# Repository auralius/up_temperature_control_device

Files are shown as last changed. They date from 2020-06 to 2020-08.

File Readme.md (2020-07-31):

This is a repository for the Universitas Pertamina's temperature control device.

The device:

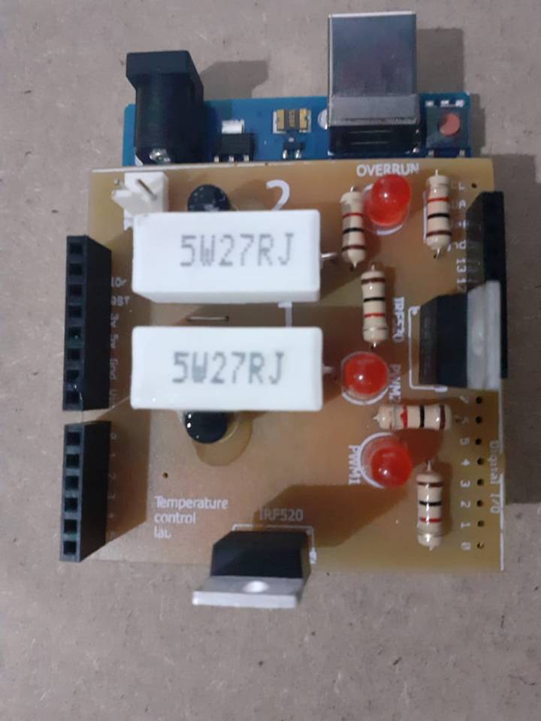
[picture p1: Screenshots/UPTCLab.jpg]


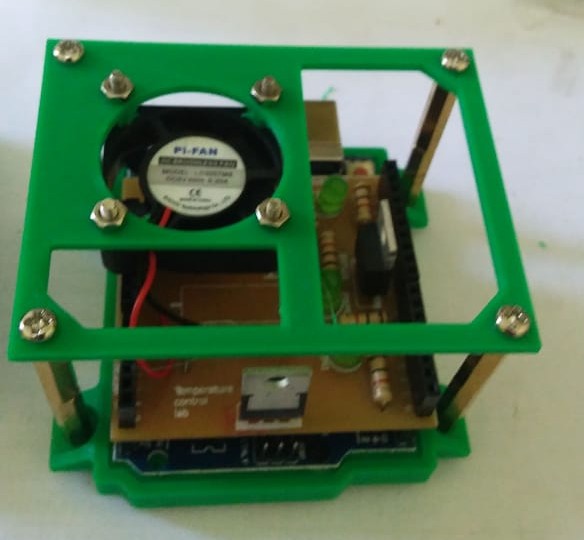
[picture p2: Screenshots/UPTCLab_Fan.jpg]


Features:
- Low cost.
- Open hardware and software, you can make your own.
- Excellent linearity at steady state condition when the temperature is below 120 degress of Celcius.
- Two heaters with two temperature sensors.
- Each heater can be heated to about 140 degrees of Celcius.
- The device is designed such that only the power resistors that become hot. The driving transistors barely get any hot.
- One of te heater can be replaced with a fan.

What you can learn with this device?
- Perform mathematical modeling, starting with the basic Time-Delay-Time-Constant (TDTC) model.
- Analyze the effect of a time delay to a system.
- Linearize the time delay model.
- Understand how a constrained input-output signal contributes to the guarantedness of system stability (a bounded-input and bounded-ouput (BIBO) system).
- Develop and tune a constant gain feedback control.
- Develop and tune a PID control.
- Develop an on-off control with hysteresis.
- Develop a Smith Predictor control.
- Develop more advance model based controls such as the Model Reference Adaptive Control (MRAC).
- Develop multiple-input and multiple-output (MIMO) models and controls.
- Perform system parameter optimizations.
- Develop an energy balance model.
- Calculate convetion rate of the fan as a function of its speed.

The software that is used is MATLAB Simulink with the Arduino support package. It is also possible to use LabVIEW with Linx libraries for the Arduino.

Here some examples:

Pade approximation of a time delay model:

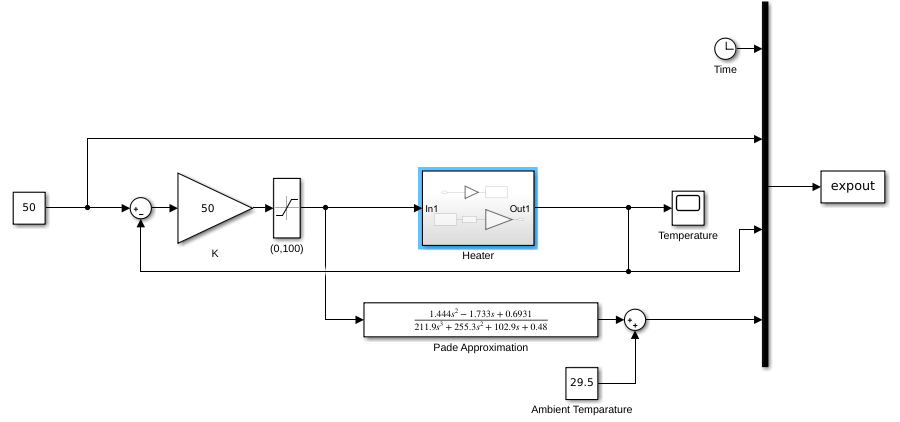
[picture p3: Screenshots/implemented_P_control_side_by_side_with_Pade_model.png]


The TDTC model:

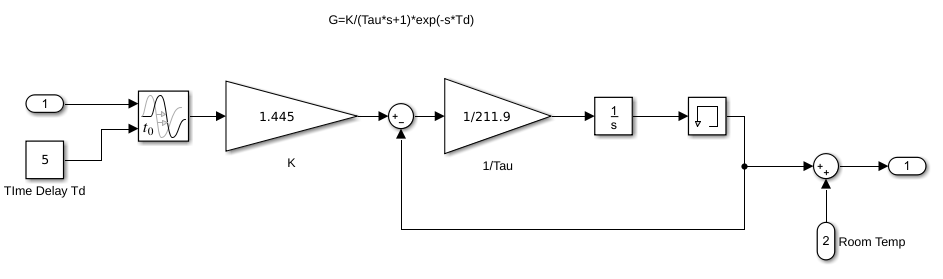
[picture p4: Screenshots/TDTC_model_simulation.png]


The on-off control with hysteresis:

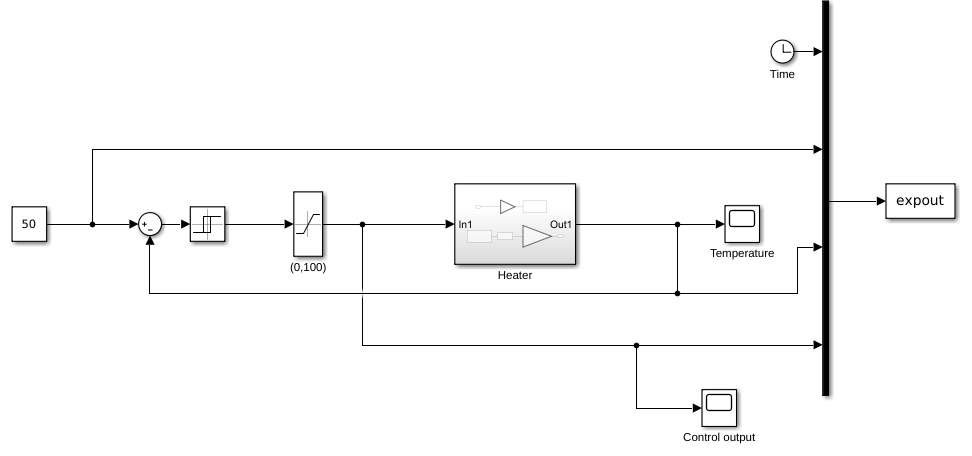
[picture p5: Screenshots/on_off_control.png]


The MRAC with the MIT rule:

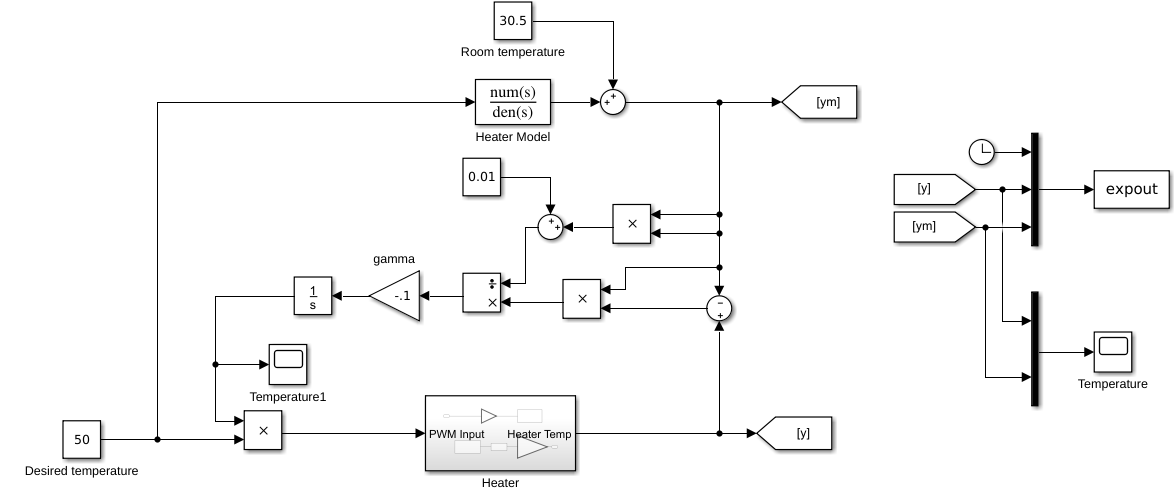
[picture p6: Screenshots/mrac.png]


You might also want to look into the Arduino TCLab from Birgham Young University, where we mainly get our inspiration from: http://apmonitor.com/pdc/index.php/Main/ArduinoTemperatureControl

There is also one from RMIT, Australia: https://journals.sagepub.com/doi/10.1177/0020720919852784

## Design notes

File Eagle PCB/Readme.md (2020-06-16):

Eagle version: 9.5.2 Education

There is a ZIP file containing the GERBER files which have been successfully sent for productions.

The schematic:

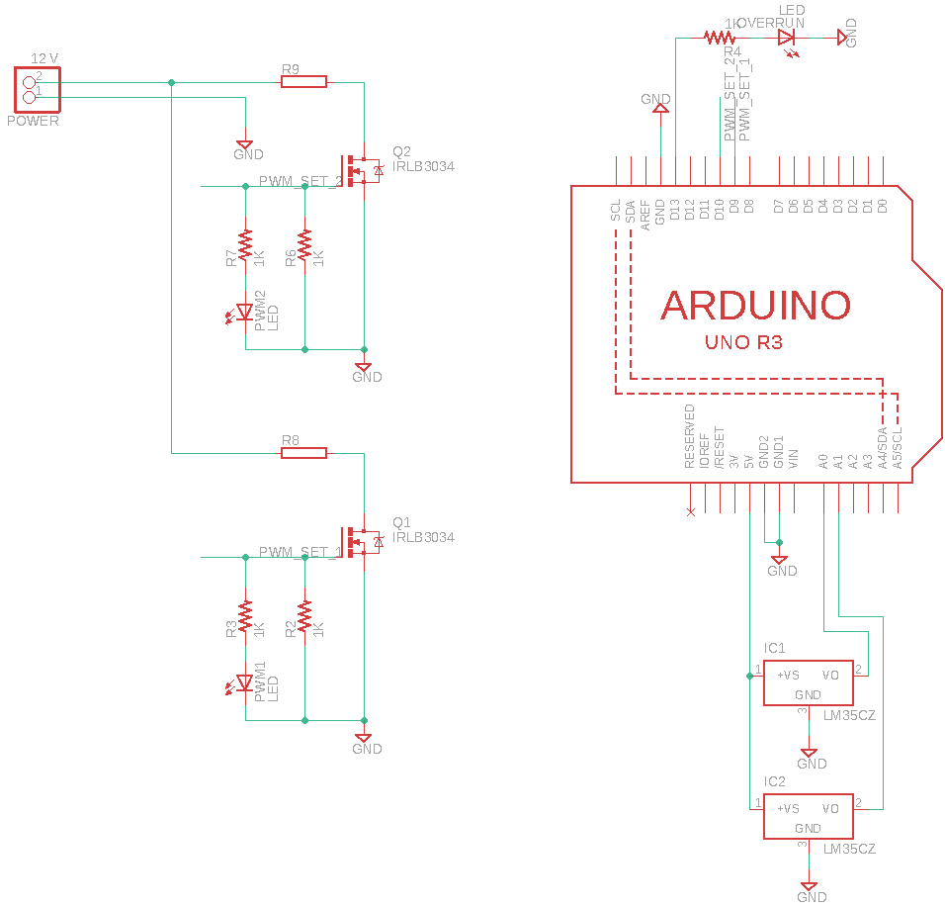
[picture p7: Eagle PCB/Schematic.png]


The PCB:

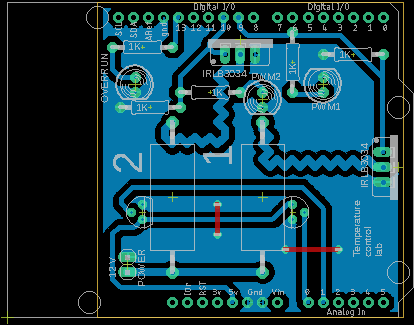
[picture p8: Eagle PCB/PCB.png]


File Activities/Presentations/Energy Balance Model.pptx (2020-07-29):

## Energy Balance Model for the Universitas Pertamina Temperature Control Device

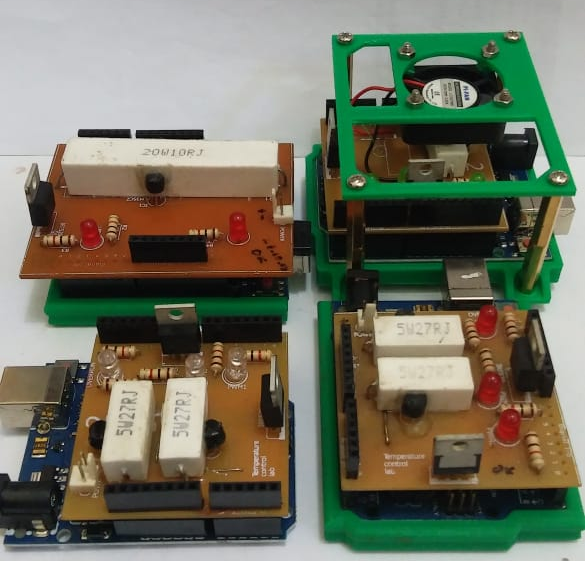
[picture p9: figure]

## Heat Dissipated by a Resistor

P=(V^2)/R
V is the voltage across the resistor
R is the resistance of the resistor
V=α V_(max)
α is the applied PWM percentage (from 0 to 1)
V_(max) is the maximum voltage ( 12 Volts)

## Heat Dissipated by a Resistor

Thus:
P=(αV_(max) ^2)/R
However, since we can not guarantee the correctness of the PWM , V_(max) and R , we then introduce a correcting factor β:
P=β(αV_(max) ^2)/R
We will use an optimization method to find β .

## Energy Balance Model

Heat in = Heat Out + Heat Stored
β(αV_(max) ^2)/R=hA(T_r −T_a )+eσA(T_r^4 −T_a^4 )+mc_r (dT_r)/(dt)

## Energy Balance Model

h is the heat transfer coefficient - W/(m^2 K)
e is the emissivity (from 0 to 1)
σ is the Stefan-Boltzman constant , the value is 5.6703×10^(−8) W/(m^2 K^4 )
c_r is the heat capacity - J/(kg K)
T_r is the temperature of the resistor - K
T_a is the ambient temperature - K

## Finding the Unknown Parameters

Rewrite the energy balance equation in the following form:
mc_r (dT_r)/(dt)=β((αV_(max) )^2)/R+hA(T_a −T_r )+eσA(T_a^4 −T_r^4 )

## Finding the Unknown Parameters

- Known values so far:
  - α is the given PWM command
  - V_(max) =12 Volts
  - R=27 Ohms
  - T_a and T_r are from measurement
  - σ=5.6703×10^(−8)
  - A=0.0008 m^2
  - m=0.005 kg
- Parameters to find:
  - C_r
  - h
  - e , from 0 to 1
  - β , probably from 0 to 1

More or less, measured with a ruler and a scale.

## Results

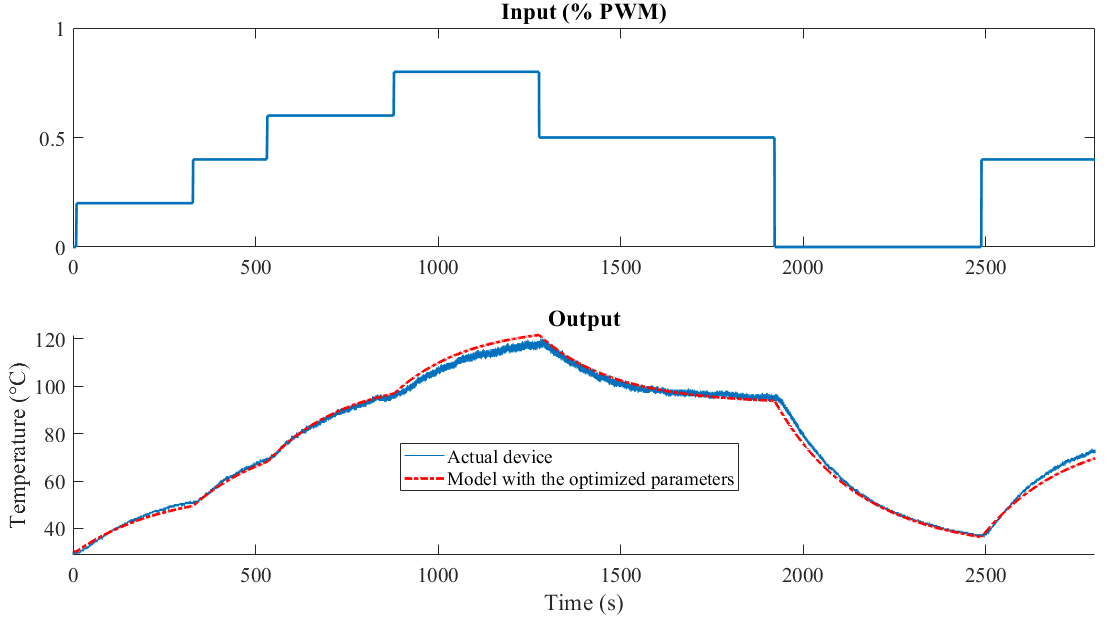
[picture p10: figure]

## Results

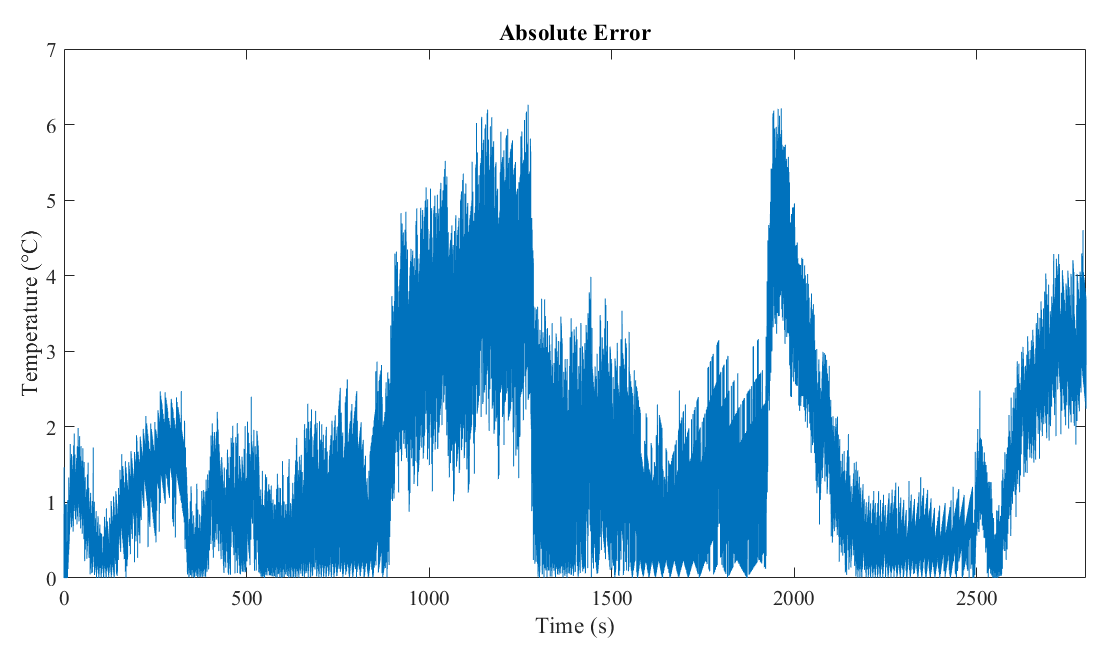
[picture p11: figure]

## Results

By using the fminsearch command (fmincon gives worse estimates)
  - C_r =1015.1584 J/(kg K)
  - h=19.7300 W/(m^2 K)
  - e=0.9047
  - β=0.5131
And the maximum value of the absolute error is less than 7℃ .

## Results

Seriously, no time delay?
Why?

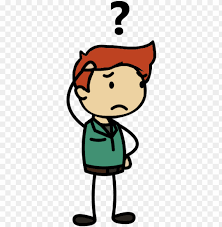
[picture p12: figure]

## Modeling Heat Transfer Coefficient by the Fan

Small fan on top the heater. The speed of the fan can be adjusted,
from 0 (no speed) to 1 (full speed).


## Energy Balance Model

The model becomes:
mc_r (dT_r)/(dt)=β((αV_(max) )^2)/R+(h_1 +γh_2 )A(T_a −T_r )+eσA(T_a^4 −T_r^4 )
h_1 is the heat transfer rate for normal convection while h_2 is by the fan.
γ is the speed of the fan (from 0 to 1).

## Results

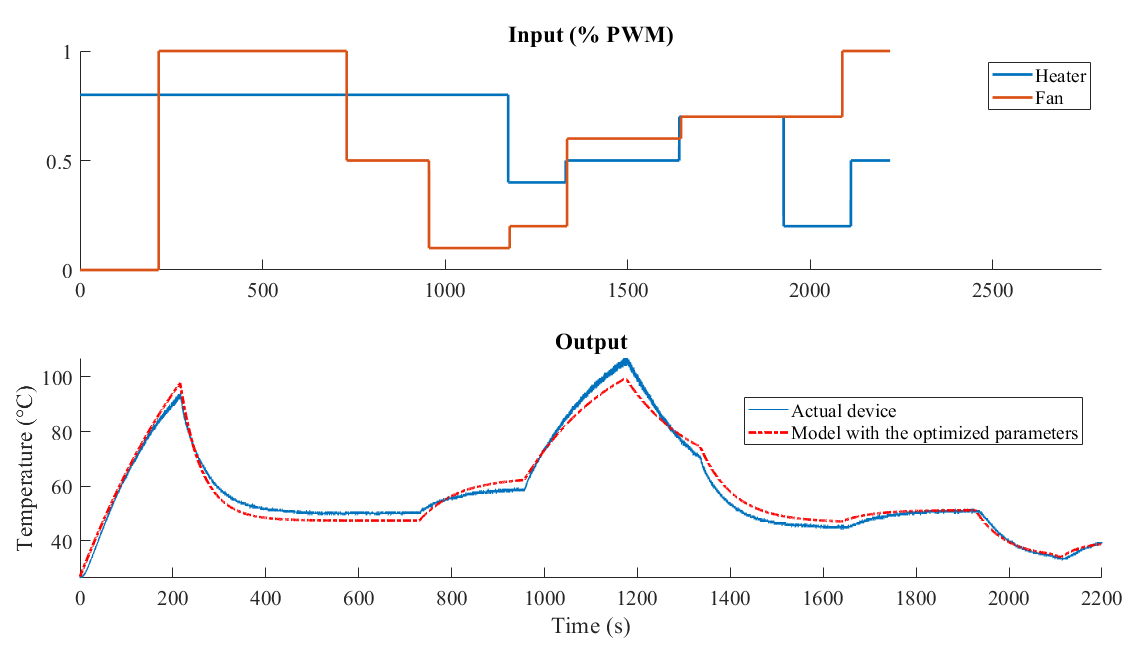
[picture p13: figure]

## Results

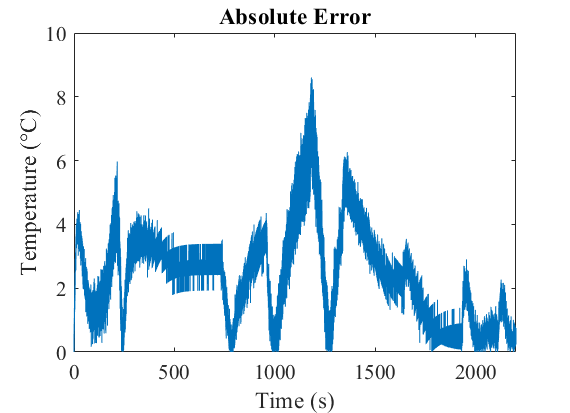
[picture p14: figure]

## Results

By using the fminsearch command:
  - C_r =1014.0626J/(kg K)
  - h_1 =9.7554W/(m^2 K)
  - h_2 =117.8434W/(m^2 K)
  - e=0.9222
  - β=0.5153
And the maximum value of the absolute error is less than 9℃ .
The other parameters get slightly readjusted. Compare them with the previous experiment.
We have some uncertainties here, every time we do the experiment, we might end up with slightly different values.

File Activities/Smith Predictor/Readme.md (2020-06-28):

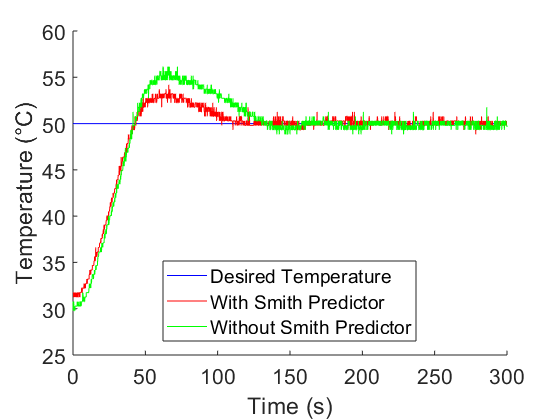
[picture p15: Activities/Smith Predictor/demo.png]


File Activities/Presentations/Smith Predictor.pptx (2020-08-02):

## Smith Predictor

ME
Universitas Pertamina
2020

## Intended Learning Outcomes

- Students learn how a mathematical model can benefit control performance of a system.
- Students can explain how time delay affects a control system performance.

## Tasks

- Implement a constant gain feedback controller and a constant gain feedback controller with Smith Predictor.
- Compare the performance of both controllers.
- Set the gain of both controller to be larger then the jω -crossing gain from the root-locus method.

## The Classical Smith Predictor [1]

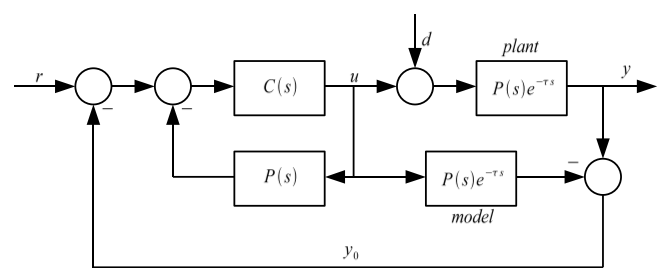
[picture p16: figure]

TC Model

TDTC Model

## Some results

Less overshoot

Less oscillations

## References

[1] O. J. M. Smith, “Closed Control of Loop with Dead Time,” Chemical Engineering Progress 53(5), pp 217-219, 1957

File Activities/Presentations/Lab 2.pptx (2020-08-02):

## First Order Plus Time Delay (FOPTD) Model or Time Delay Time Constant (TDTC) model

ME
Universitas Pertamina
2020

## Step response Experiment

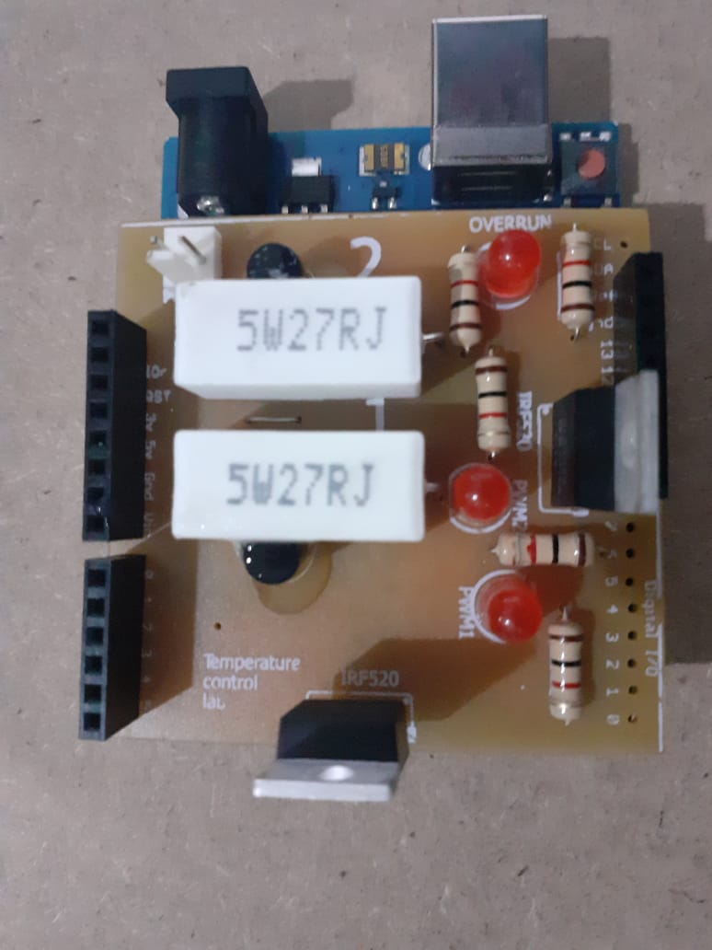
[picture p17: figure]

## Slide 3

- Apply an input of 50%.
- Run the Simulink, record the time, the input and the output.
- Run for at least for 1500 seconds.

## 50% of Input PWM

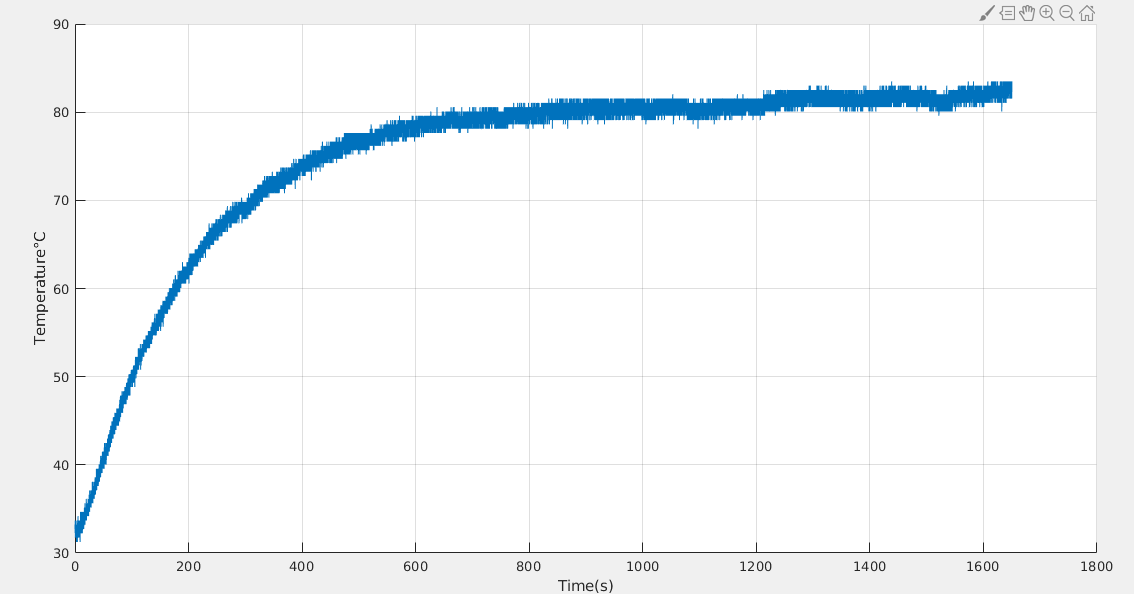
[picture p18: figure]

## Temperature offset has been removed

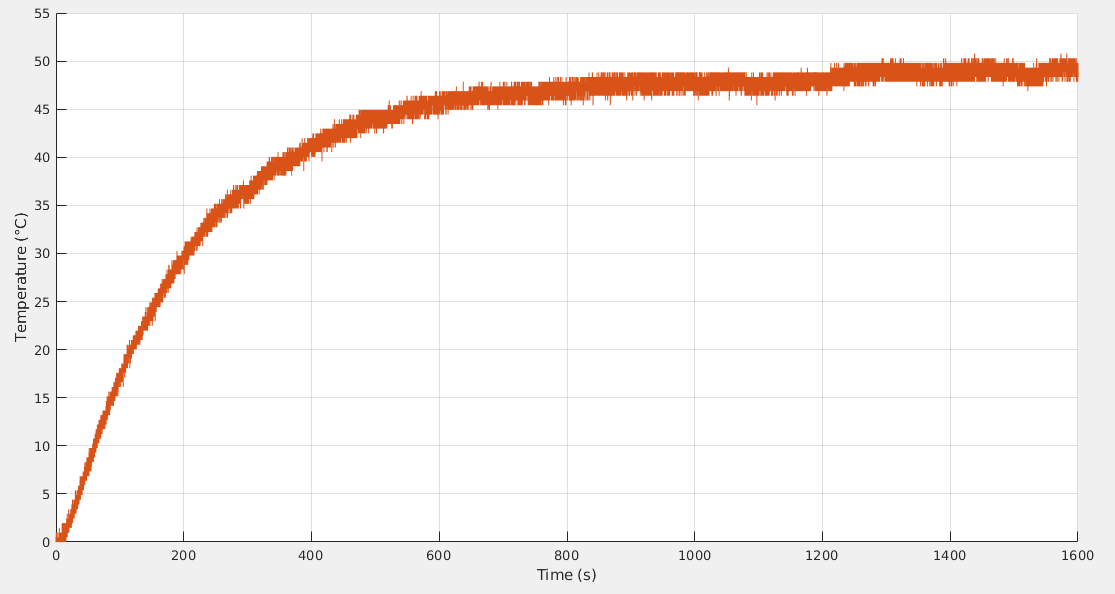
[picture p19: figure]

y_(ss)

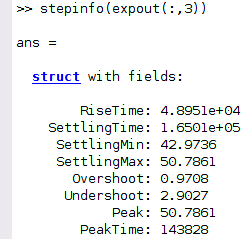
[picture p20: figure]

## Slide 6

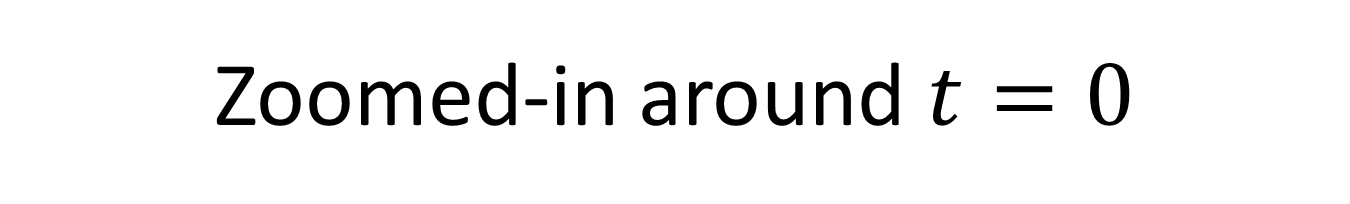
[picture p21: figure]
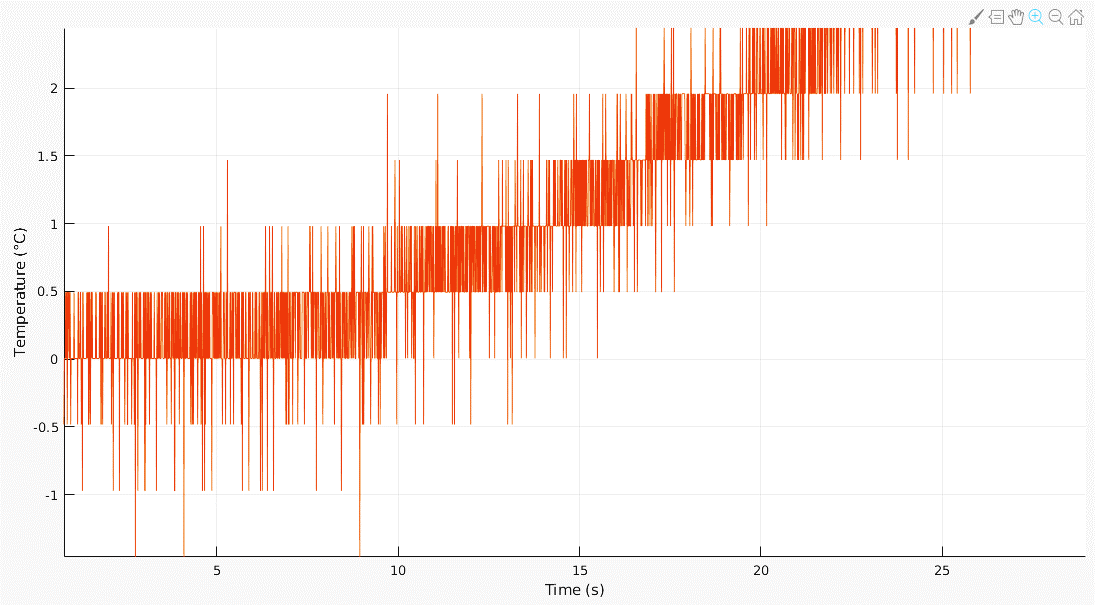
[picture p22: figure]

Time delay

θ=10

y_0

Input starts at t=0

## The TDTC model

G(s)=K_(ss) (e^(−θs))/(τs+1)

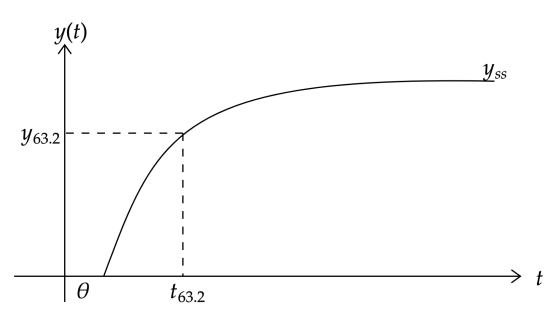
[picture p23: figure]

## Find all the parameters

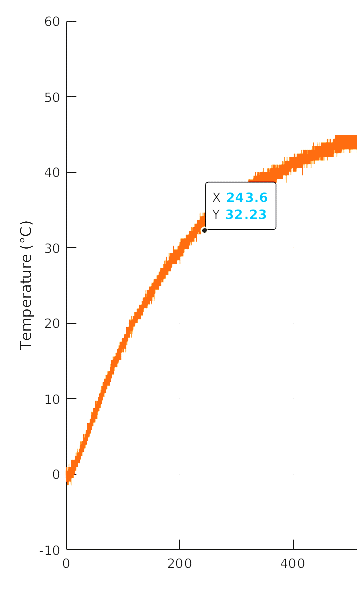
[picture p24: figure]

y_(ss) =51
θ=10
y_63.2 =63.2%×51=32.23
t_63.2 =243.6=τ
K_(ss) =51/50=1.02

τ

## Results

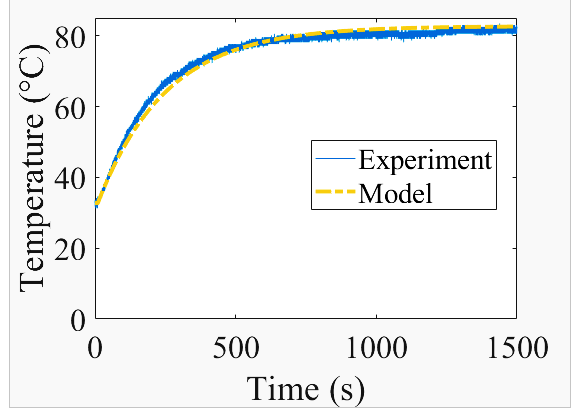
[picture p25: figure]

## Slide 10

- Calculate the absolute error (for every time point) and plot the error.
- Can you also find the integral of the absolute error (the area under the curve that you just found)?

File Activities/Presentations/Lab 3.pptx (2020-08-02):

## Lab 3

Linearization of Time Delay
Root Locus

## Prelab

K_(DC) =1.02
θ=10 secs
τ=243,6 secs
- Based on the parameters write down the model:
G(s)=1.01/(243.6s+1)e^(−10s)

## Activity 1

- Let’s first exclude the time delay in our model, and draw the root locus:

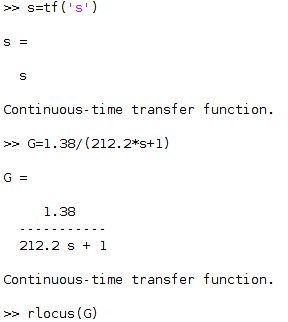
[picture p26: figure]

## Activity 1

- Can the closed loop system go unstable? Why?

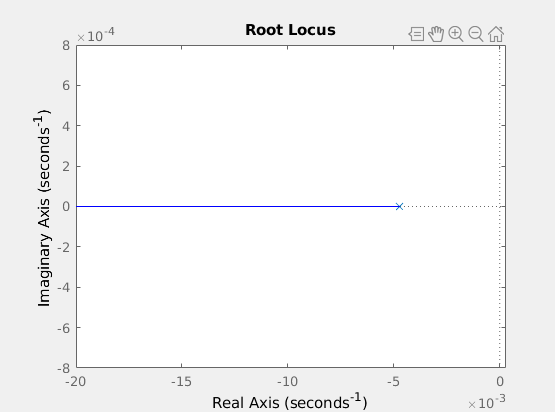
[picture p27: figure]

## Activity 2

- Let’s now include the time delay in our model:
G(s)=1.01/(243.6s+1)e^(−10s)
- However, we can not draw the root locus as MATLAB does not have such feature of drawing root locus of a nonlinear system.

## Activity 2

- We will do a Padé approximation to generate a linear system that is quite close to our actual system.

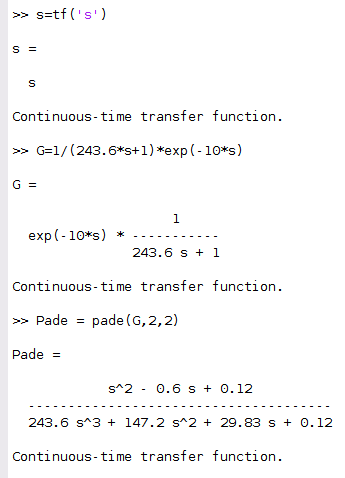
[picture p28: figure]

## Activity 2

- Now, we have a new system:
G=(s^2 − 0.6 s + 0.12)/(243.6 s^3 +147.2 s^2 +29.83 s + 0.12)
- Therefore, now we can draw the root locus:

## Activity 2

- Can the system go unstable? Why?

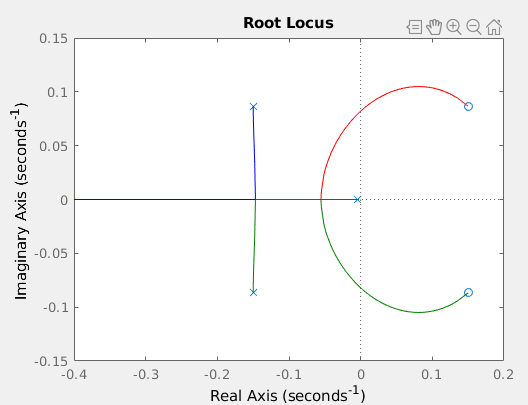
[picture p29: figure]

jω− crossings

Find the K at jω− crossings!

## Activity 2

- Now, briefly summarize how time delay affects a system stability.
- Simulate the closed loop system using both Pade and TDTC model for K>K_(jω−crossings)
  - Remember that root locus actually analyze the closed-loop system of a given open-loop system.

## Activity 2

- Can you see how Pade actually linearize the nonlinear TDTC model?
  - Do you remember the Gibb’s phenomenon?

## Activity 3

- Let’s compare the model and the real system in real time:

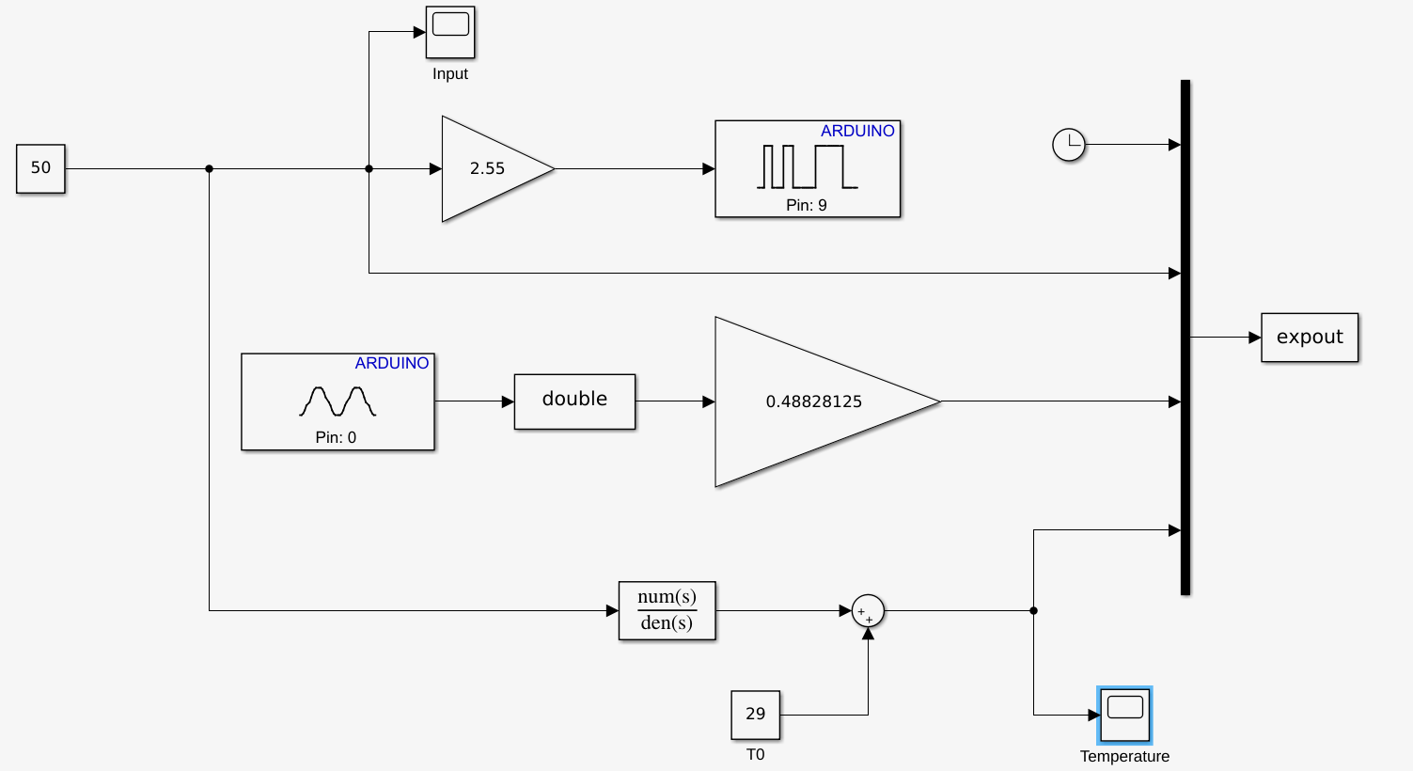
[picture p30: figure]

Use the transfer function block in Simulink,
Enter the coefficients for the numerator and denumerator:

Padé model

## Activity 3

Padé model

## Activity 3

- Find out the ambient temperature first.
- You might need to reduce the sampling time to 10ms. Check if the overrun LED is on.


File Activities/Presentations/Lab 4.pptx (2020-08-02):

## Constant Gain Feedback Controller and On/Off Controller with Hysteresis

## Constant Gain Feedback Controller

A picture containing screenshot Description generated with very high confidence

## On/Off Controller with Hysteresis

A close up of a clock Description generated with high confidence
A picture containing game Description generated with very high confidence

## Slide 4

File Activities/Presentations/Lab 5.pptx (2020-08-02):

## Model Reference Adaptif Control (MRAC)

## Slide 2


## MIT Rule


(dθ)/(dt)=−γy_m e

## Modified MIT Rule


(dθ)/(dt)=(−γy_m e)/(α+y_m ^2)

## Modified MIT Rule


## Results


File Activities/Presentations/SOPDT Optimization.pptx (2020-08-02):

## Modelling a Thermal Response as 1-DOF Vibratory System

ME
Universtitas Pertamina
2020

## Intended Learning Outcomes

- Students can derive the mathematical model of a thermal system by using data-driven methods.
- Students can simulate a thermal system and compare the simulation to the real process.
- Student can analyze the derived model and gain knowledge on the real system through the model.
- Students can understand the analogy of a vibratory system and a thermal system.

## 1-DOF Vibartory System

A 1-DOF vibartory system with input delay:
M(d^2 T(t))/(dt)+B(dT(t))/(dt)+KT=u(t−θ)


K

M

u(t−θ)

B

T

## Hariott’s Method for an Overdamped Second Order System

- Hariott’s method for the inital guess:
(T(s))/(U(s))=(e^(−Ls) K_(ss))/((τ_1 s+1)(τ_2 s+1))
Hariott’s method estimates the L,τ_1 ,τ_2 and K_(ss) .
The Hariott’s method is quite complicated. A MATLAB script has been provided for this purpose. If there is time available, we shall revisit the Hariott’s method as it is a well known method in industrial process control.

## Parameter Optimization for the Vibratory System

- Convert the Hariott’s model into:
(T(s))/(U(s))=(e^(−θs))/(Ms^2 +Bs+K)
- Use MATLAB unconstrained optimization function to estimate M, B, K and θ with the intial values provided by the Hariott’s method.
- A MATLAB script has also been provided for the optimization process.

## The Optimized Parameters

M=1622.5 Ns^2 /°C
B=186.8Ns/°C
K=0.9 N/°C
θ=10.2 s
Do the units look funny?

K

M

u(t−θ)

B

T(t)

## State-Space Form

[T(t)T(t)]=[0, 1−K/M, −B/M][T(t)T(t)]+[01/M]u(t−θ)
[T(t)T(t)]=[0, 1−0.115, −5.547×10^(−4) ][T(t)T(t)]+[06.163×10^(−4) ]u(t−θ)
y=[1, 0][T(t)T(t)]

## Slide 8

Hariott’s method actually works very well!

## Approximation of the Delayed System by Taylor Series Expansion

u(t−θ)=u(t)−θu(t)+1/2θ^2 x(t)+⋯
Therefore,
T(t)=K/MT(t)+B/MT(t)+1/M(u(t)−θu(t)+1/2θ^2 x(t)+⋯)
Can you implement it in your Simulink (up to the first order approximation only)?

## Further Ideas

- What can we do with this vibratory model?
  - Think of something, write them down in your report.

## Activity

- Apply a step input to your system, i.e. 50% PWM input
- Log both data, input and output. It is also recommended to log the time.
- Check the provided m-files: for the Hariott method and for the optimization process.
- With the found parameters, simulate the system side-by-side with the actual system. Apply any arbitrary input and observe the output.

## Activity

- Calculate the RMS eror between the simulation and the real system. Provide the plots in your report. Report the parameters of your system too.
- A Google sheet will be provided where everyone can report their parameters. We will see how different these parameters are among groups.

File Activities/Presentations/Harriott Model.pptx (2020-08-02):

## Harriott’s¹ Model for Overdamped Systems

ME
Universitas Pertamina
2020

¹Harriott, P., Process control, McGraw‐Hill, New York (1964)

## Overdamped Second Order System

General form:
G(s)=(K_(ss) e^(−θs))/((τ_1 +1)(τ_2 +1)), τ_1 >τ_2
K_(ss) is the system steady-state gain.
τ_1 and τ_2 are the time constants.
θ is the time delay.

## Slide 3

The acquired step response:

y_(ss)

y_72

y_z

Remove the offset

θ

t_z

t_72

K_(ss) =(y_(ss))/(Amplitude of the step input)

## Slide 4

Remove the offset

Estimate θ, y_(ss) , K_(ss)

Find t_72 from the step response plot

Find y_z

t_z =0.4t_72 +0.6θ

∑ T=(T_1 +T_2 )=(t_72 −θ)/1.25

(y_z)/(y_(ss))<0.27

(y_z)/(y_(ss))>0.4

yes

Increase θ

no

T_1 =z∑ T
T_2 =∑ T−T_1

yes

Decrease θ

no

Find z from the Hariot’s plot

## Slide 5


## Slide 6


http://www.users.abo.fi/khaggblo/PDC/PDC5milver.pdf

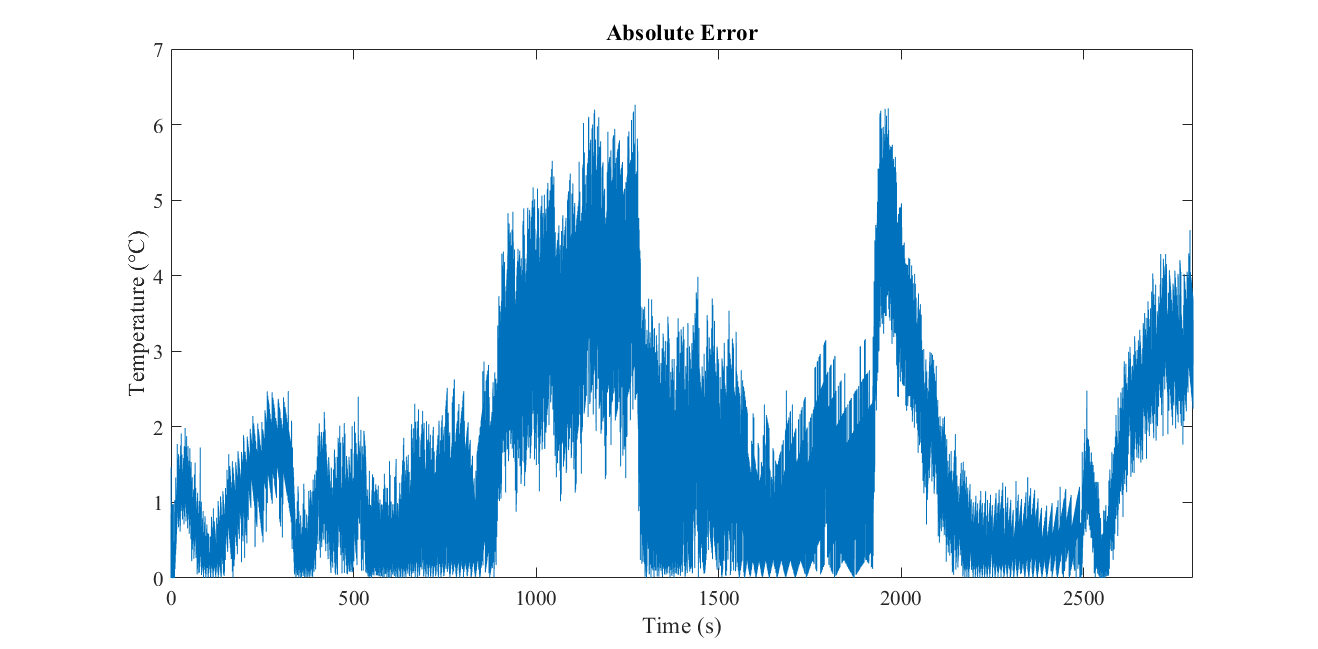
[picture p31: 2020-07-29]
Activities/Energy Balance/absolute_error.png

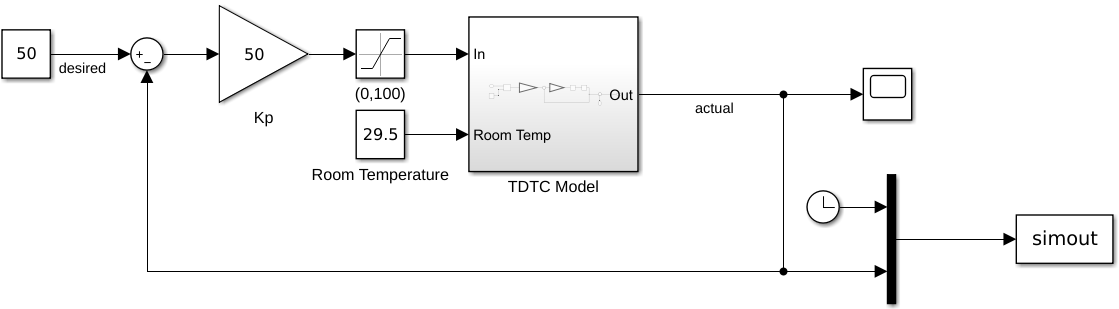
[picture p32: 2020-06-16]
Screenshots/TDTC_with_P_control_simulation.png

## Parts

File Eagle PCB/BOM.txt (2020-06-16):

LED 5MM                 3 pcs
LM35                    2 pcs
R 1KOhm 0.5 Watt        5 pcs
R 27Ohm 5 Watt          2 pcs
IRLB3034                2 pcs
Header 2 pin            1 pcs
Arduino Uno             1 pcs
Stacking header 6 pin   1 pcs
Stacking header 8 pin   2 pcs
Stacking header 10 pin  1 pcs

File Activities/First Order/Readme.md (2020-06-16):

logged_data.bin is the logged data from real experiment. It is a binary file, taken with the provided LabVIEW program. The logged file has 3 rows of data. Each row represents time, input, and output, repectively. The column itself represents the time point. The data was collected at 100Hz of sampling rate.

The main file is: optimized_tdtc.m

Run the main file to get what is really happening. 

For example, the optimization gives:
xf = [1.09633931848365   232.060134197884   9.49364907247007]; 

The first one is the steady state gain (Kss), the second one is the time constant (Tau), and the last one is the time delay (theta). Thus, the otimized model is:

``
T(s)/U(s) = Kss/(Tau*s+1)*exp(-s*theta) = 1.096/(232.060*s+1)*exp(-s*9.494)
``

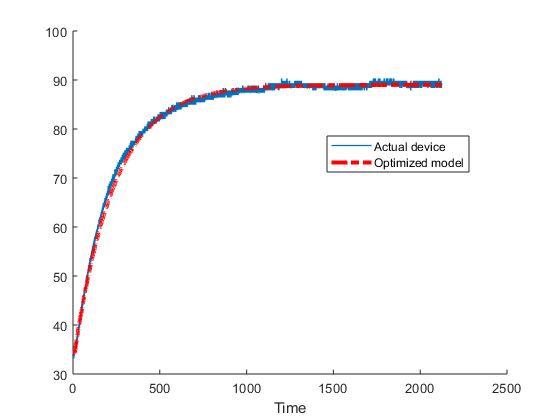
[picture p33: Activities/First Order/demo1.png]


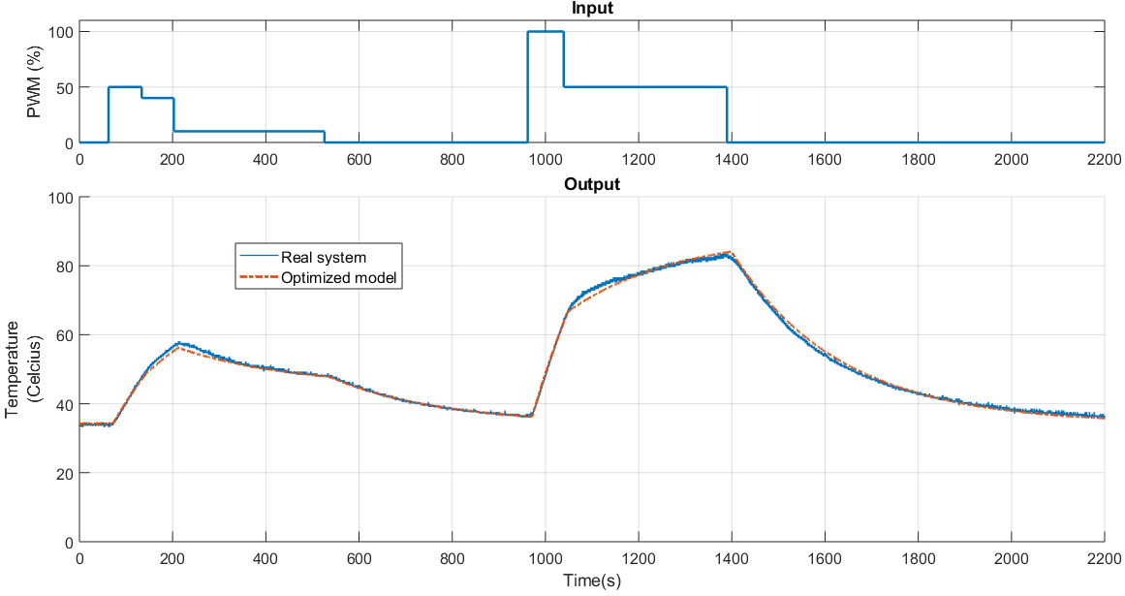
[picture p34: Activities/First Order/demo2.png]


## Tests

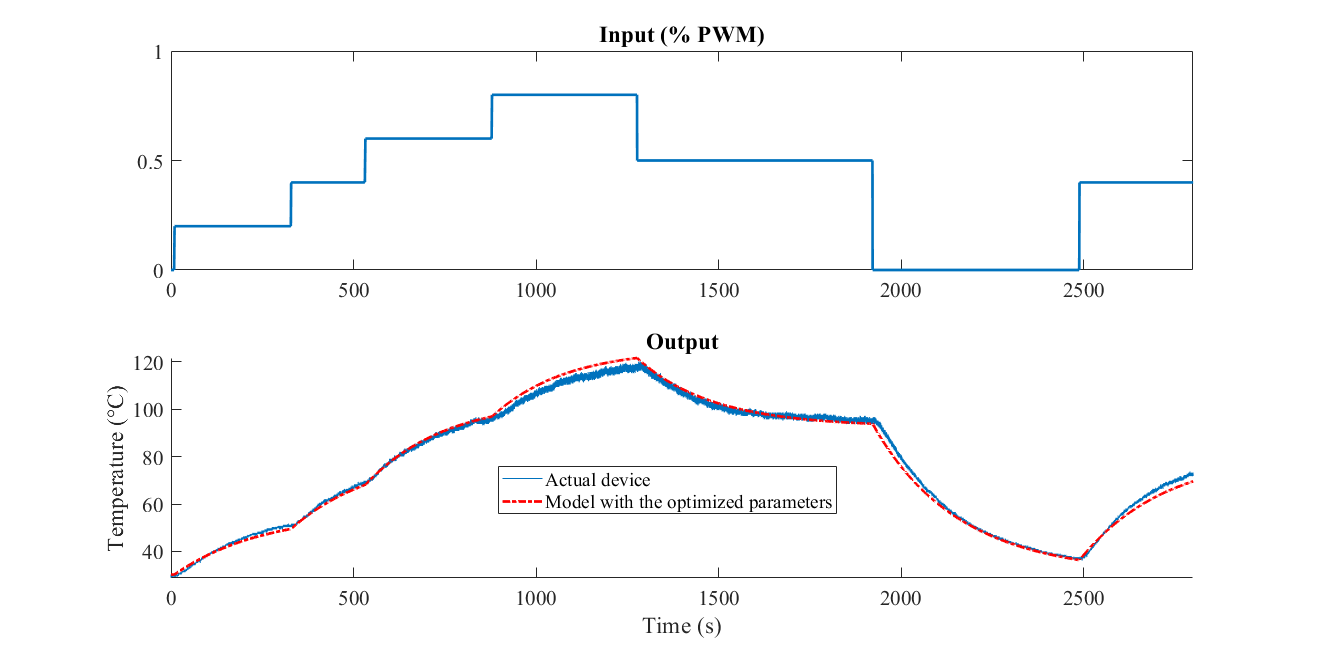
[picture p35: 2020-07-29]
Activities/Energy Balance/result.png

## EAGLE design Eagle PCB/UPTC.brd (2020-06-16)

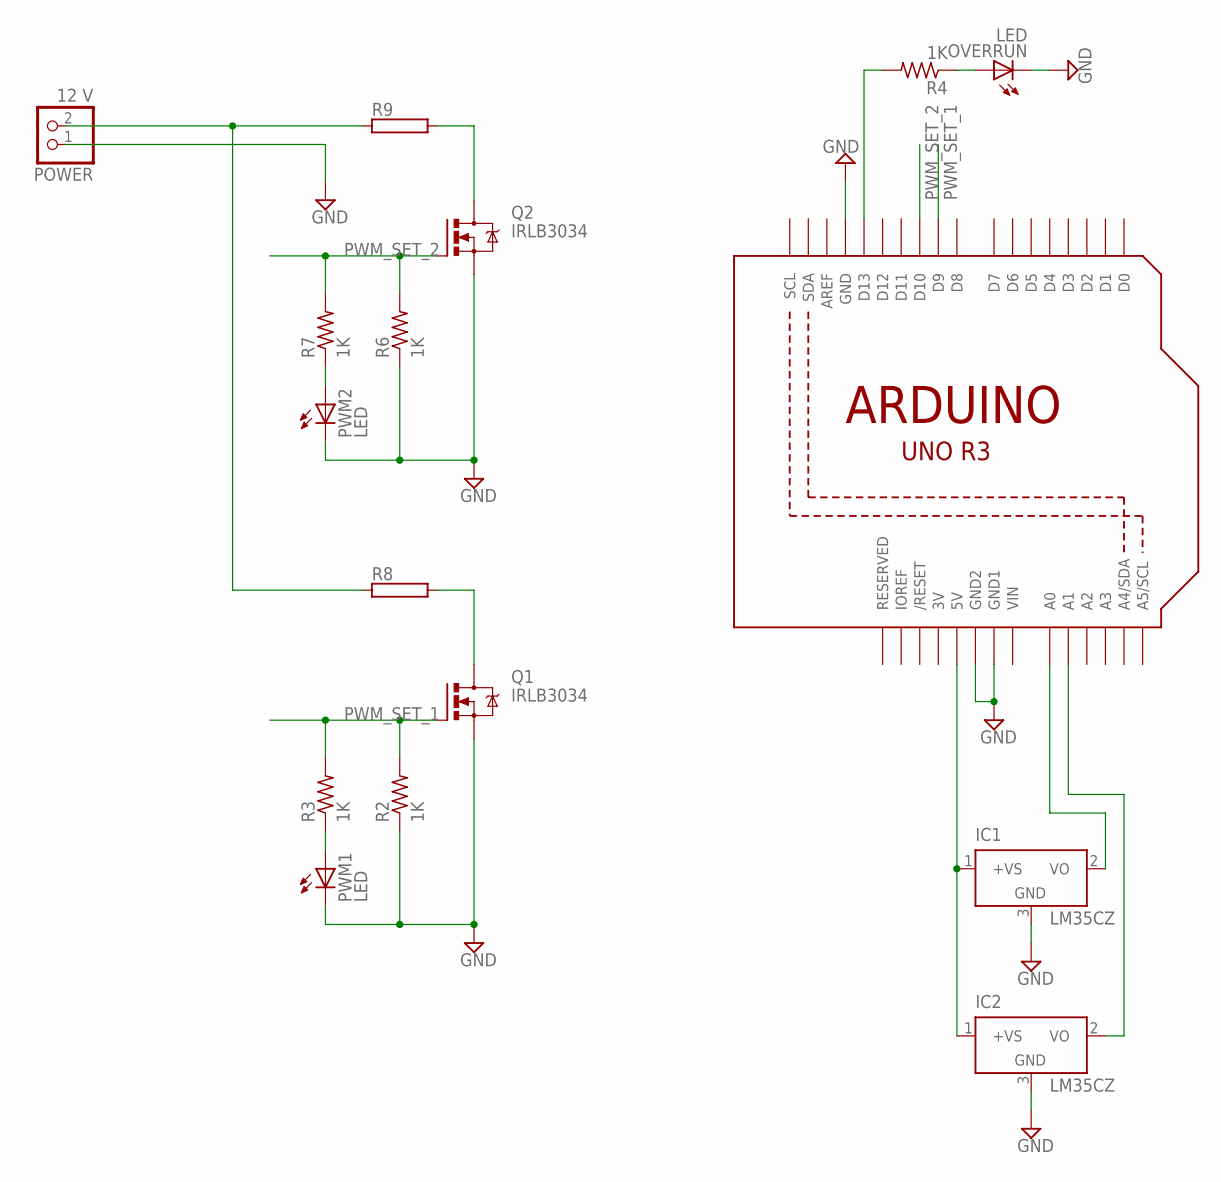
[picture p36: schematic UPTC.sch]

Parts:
IC1, IC2: LM35CZ; TO92
OVERRUN: LED; LED5MM
POWER: 12 V; 1X02
PWM1, PWM2: LED; LED5MM
Q1, Q2: IRLB3034; TO220BV
R2, R3, R4, R6, R7: 1K; 0207/10
R8, R9: RAC05; AC05
U2: ARDUINOR3-BPLACE

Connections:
3V: U2.3V
GND: IC1.3 (GND), IC2.3 (GND), OVERRUN.K (C), POWER.1, PWM1.K (C), PWM2.K (C), Q1.S, Q2.S, R2.1, R6.1, U2.GND, U2.GND1, U2.GND2
unnamed: Q1.D, R8.2
unnamed: IC1.1 (+VS), IC2.1 (+VS), U2.5V
unnamed: IC1.2 (VO), U2.A0
unnamed: R4.2, U2.D13
unnamed: PWM1.A, R3.1
unnamed: OVERRUN.A, R4.1
unnamed: IC2.2 (VO), U2.A1
unnamed: Q2.D, R9.2
unnamed: PWM2.A, R7.1
unnamed: POWER.2, R8.1, R9.1
PWM_SET_1: Q1.G, R2.2, R3.2, U2.D9
PWM_SET_2: Q2.G, R6.2, R7.2, U2.D10
VIN: U2.VIN

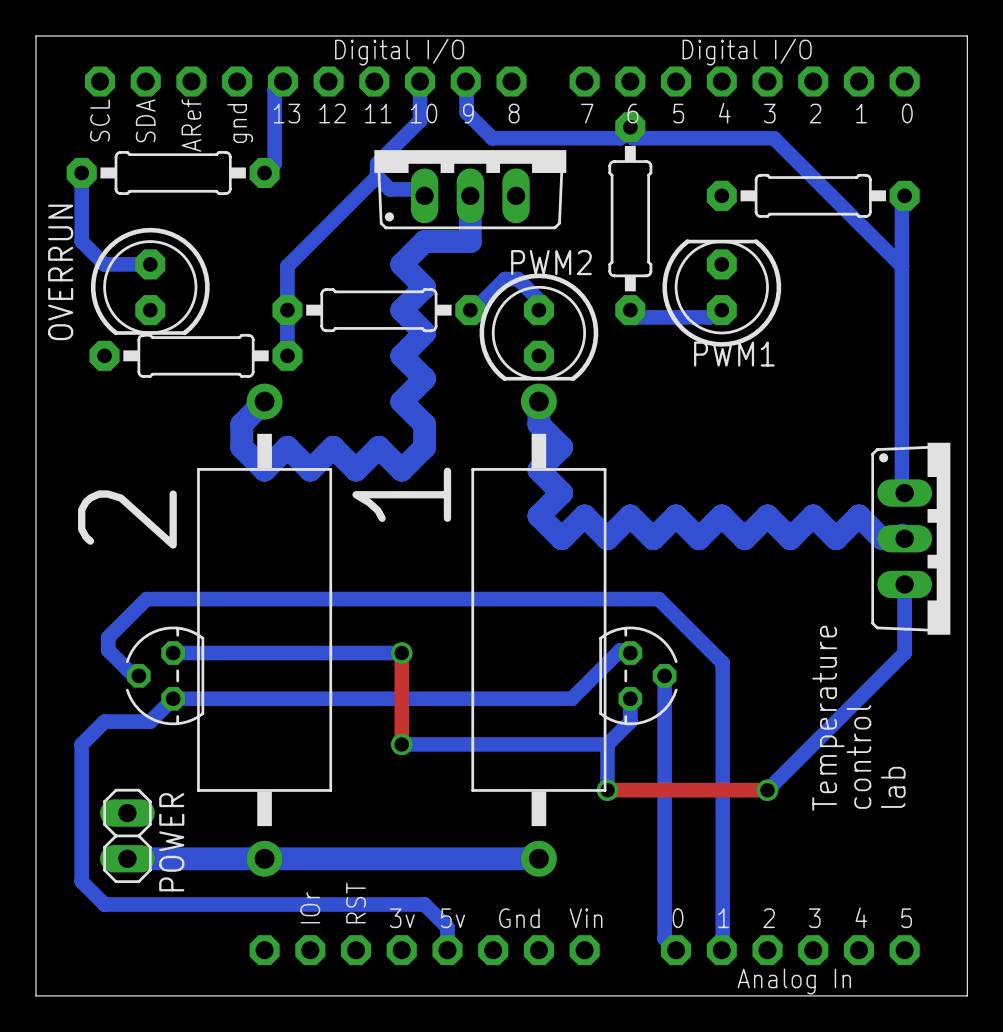
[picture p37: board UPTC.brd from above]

Board: 2 copper layers, 51.7 x 53.3 mm, 16 parts (0 on the bottom side), 13 nets.
